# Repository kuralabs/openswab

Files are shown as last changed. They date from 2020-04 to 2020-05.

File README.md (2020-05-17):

# OpenSwab - Hisopo Nasofaringeal (NP) para COVID-19

[][cc-by-sa]

[English Version](README.en.md)

[Versión en PDF](doc/OpenSwab-Rev-4-KuraLabs.pdf)

## Descargo de responsabilidad

OpenSwab fue construido, diseñado y puesto a disposición en el contexto de una
escasez global de suministros y equipos para combatir la crisis de salud
pública causada por la enfermedad por Coronavirus (COVID-19). Este diseño,
junto con muchos otros, está siendo revisado actualmente por las autoridades
sanitarias y está siendo sometido a ensayos clínicos.

**SIN EMBARGO, NO HA SIDO PROBADO, VALIDADO O APROBADO TOTALMENTE POR NINGUNA
ORGANIZACIÓN. POR LO TANTO, DEBE SER CONSIDERADO UN PROTOTIPO.**

KuraLabs S.R.L comparte estos diseños en buena voluntad con la comunidad global
en un momento de crisis con el fin de enfrentar las brechas en la respuesta
regional y ofrecer un método alternativo para producir hisopos de prueba
necesarios utilizados para probar casos sospechosos de COVID-19 que están
siendo requeridos con urgencia. En consecuencia, KuraLabs S.R.L no asume
**NINGUNA RESPONSABILIDAD** por las lesiones o daños directos, indirectos o
incidentales sufridos como resultado del uso, mal uso o dependencia de estos
hisopos de prueba y/o de la información y el contenido de este sitio web.

La principal prioridad para KuraLabs S.R.L es el bienestar de los pacientes. En
consecuencia, es responsabilidad de quien quiera utilizar OpenSwab de enviarlo
para su aprobación, revisión y ensayos clínicos respectivos con el fin de
obtener una licencia, autorización o aprobación por parte de su autoridad
reguladora local antes de usar estos hisopos en el contexto médico. Al decidir
voluntariamente usar y/o producir los diseños de OpenSwab, usted asume el
riesgo de cualquier lesión resultante. **ÚSELO BAJO SU PROPIO RIESGO**.

## Descripción

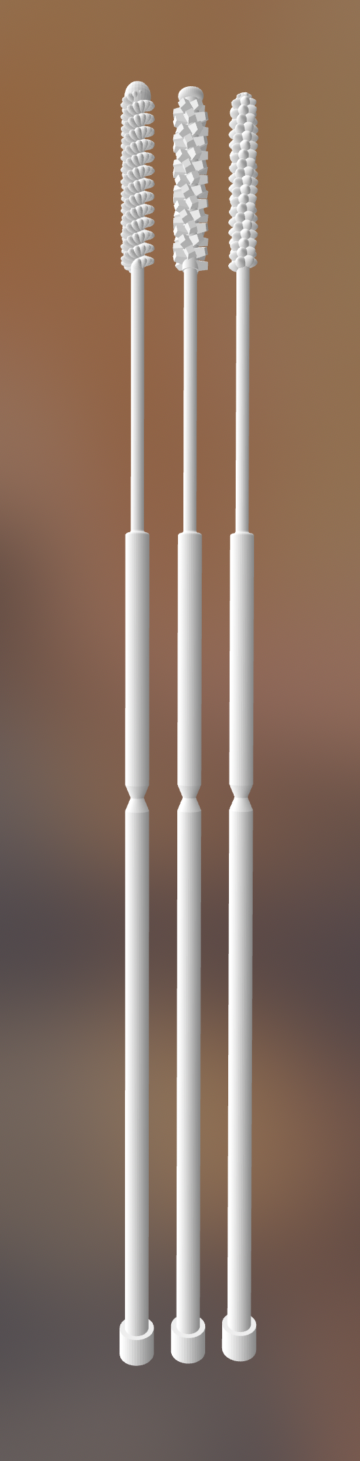
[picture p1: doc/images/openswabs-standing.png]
OpenSwab Render


OpenSwab es un prototipo de hisopo nasofaringeal (NP) diseñado para recolectar
muestras y realizar pruebas de COVID-19.

Es un hisopo fino y flexible, el cual es insertado en la cavidad nasal de forma
paralela a la parte inferior de la fosa nasal hasta que la cabeza del hisopo
toque la pared de la nasofaringe. Al llegar a la pared, se procede a realizar
pequeñas rotaciones de forma que la cabeza del hisopo recolecte el material
biológico requerido para proceder a realizar la prueba COVID-19.

Los hisopos utilizados para pruebas COVID-19 no pueden estar hechos de
materiales como algodón o madera, ya que los mismos afectan el ARN de la
muestra tomada.

Debido a la precisión y exactitud requerida, este hisopo fue diseñado para ser
impreso por una impresora 3D de tecnología SLA (Estereolitografía) utilizando
resina de curado ultravioleta (UV) biocompatible de Clase I (uso de corto plazo)
resistente al calor para su posterior esterilización en un autoclave.

Al momento de escribir este artículo, existe una escasez global de equipo de
protección personal y otros suministros médicos, incluidos los hisopos de
prueba. Estos hisopos fueron diseñados y creados en un esfuerzo por
proporcionar una posible solución alternativa a este problema.

La propiedad intelectual de este diseño se encuentra bajo una licencia
[CC BY-SA 4.0][cc-by-sa] por lo que puede ser utilizado, producido, modificado
y comercializado libremente. Puede referirse a la sección de licencia o
contactar al equipo de OpenSwab para más información.

<br clear="right"/>

## Fotos

<p align="center">
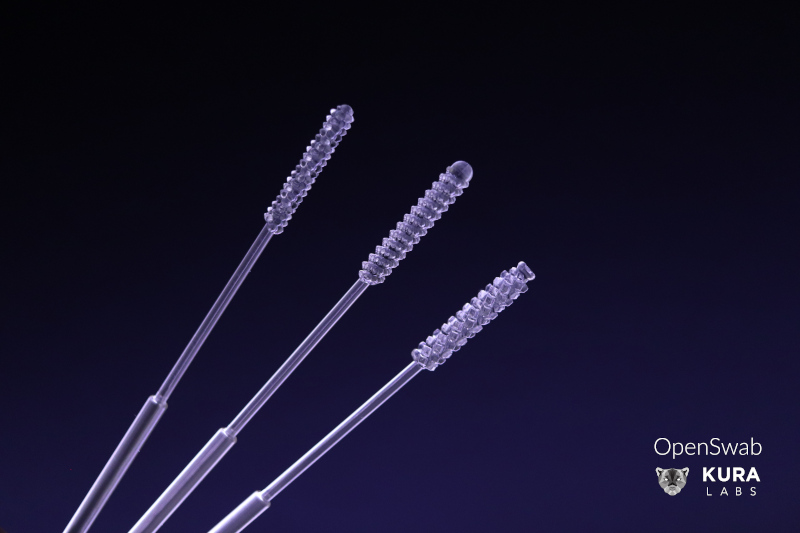
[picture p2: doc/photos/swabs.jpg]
OpenSwab swabs
  
</p>

<br clear="right"/>

<p align="center">
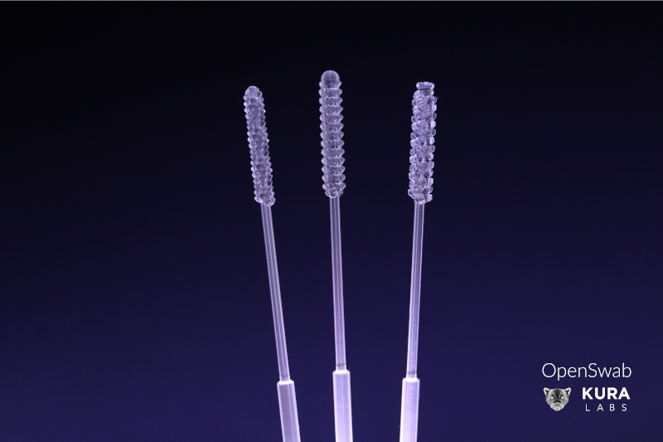
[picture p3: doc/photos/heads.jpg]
OpenSwab heads
  
</p>

<br clear="right"/>

<p align="center">
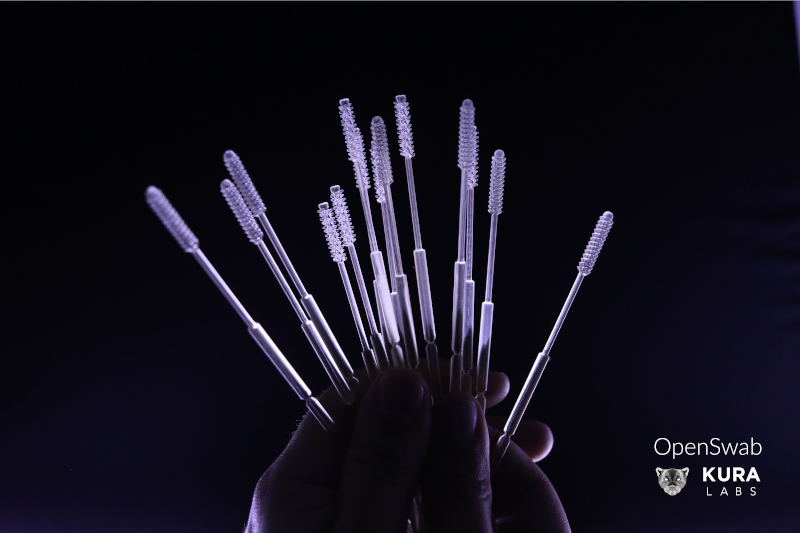
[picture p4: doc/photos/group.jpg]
OpenSwab group
  
</p>

<br clear="right"/>

## Especificaciones Técnicas

OpenSwab ofrece cuatro modelos con diferentes versiones de cabeza para la
recolección de muestras, denominadas "Bristle", "Pyramid", "Vitellus".

<p align="center">
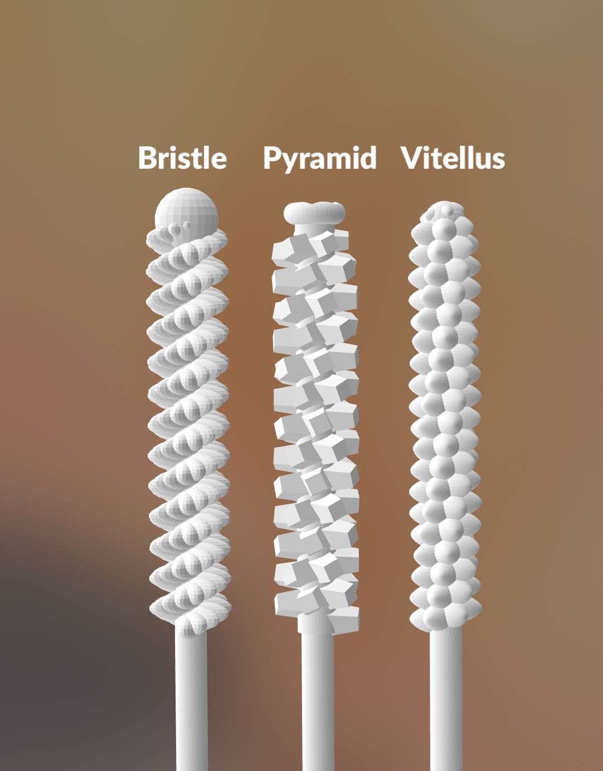
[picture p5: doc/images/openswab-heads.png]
OpenSwab Heads
    
</p>

| Modelo             | Bristle         | Pyramid                      | Vitellus        |
| ------------------ | --------------- | -----------------------------| ----------------|
| *Público meta*     | Adulto          | Adulto                       | Adulto          |
| *Uso*              | Nasofaringeal   | Nasofaringeal                | Nasofaringeal   |
| *Altura total*     |         145.0mm |                      145.0mm |         145.0mm |
| *Material*         | Resina UV 405nm | Resina UV 405nm              | Resina UV 405nm |
| *Esterilización*   | Autoclave       | Autoclave                    | Autoclave       |
|                                               **Cabeza**                              |
| *Textura*          | Hojuela         | Pirámide truncada            | Elipsoide       |
| *Patrón*           | Helicoidal      | Helicoidal                   | Helicoidal      |
| *Terminación*      | Esférica        | Toroide con estrella convexa | Esférica        |
| *Diámetro interno* |           1.5mm |                       1.85mm |           1.5mm |
| *Diámetro externo* |           3.9mm |                        3.9mm |           3.9mm |
| *Largo*            |          20.0mm |                       20.0mm |          20.0mm |
|                                            **Cuello flexible**                        |
| *Diámetro*         |           1.5mm |                        1.5mm |           1.5mm |
| *Largo*            |          30.0mm |                       30.0mm |          30.0mm |
|                                               **Cuerpo**                              |
| *Diámetro*         |          2.75mm |                       2.75mm |          2.75mm |
| *Largo*            |          95.0mm |                       95.0mm |          95.0mm |
| *Punto de quiebre* |          95.0mm |                       95.0mm |          95.0mm |

Todas estas dimensiones son fácilmente configurables.
Ver sección de [Configuración del Producto](#configuracion-del-producto).

## Características del Producto

- Punto de Quiebre: Al finalizar la toma de la muestra, el punto de quiebre
  permite separar la parte del hisopo que se encarga de la recolección del
  material biológico para así almacenarla en el tubo de muestra.

  El punto de quiebre también funciona como guía visual para indicarle al
  personal médico que debe evitar manipular el hisopo pasando el mismo, tanto
  para evitar la contaminación de la muestra como para prevenir cualquier tipo
  de exposición.

- Material de Construcción: Los hisopos utilizados para pruebas COVID-19 no
  pueden estar hechos de materiales como algodón o madera, ya que los mismos
  afectan el ARN (Ácido Ribonucléico) de la muestra tomada.

  Es por eso que OpenSwab está diseñado para ser impreso en una impresora 3D de
  tecnología SLA (Estereolitografía) utilizando resina de curado ultravioleta
  (UV) biocompatible de Clase I (uso de corto plazo) resistente al calor para
  su posterior esterilización en un autoclave.

- Diseño anatómico: Hisopo diseñado con un cuello delgado y flexible que se
  adapta a las fosas nasales del paciente por lo que se reduce el malestar y
  facilita el posicionamiento de la cabeza en el lugar adecuado por parte del
  personal médico. La cabeza cuenta además con un patrón helicoidal que
  facilita la introducción, el retiro y la acción giratoria propia del frotis.

- Diseño ergonómico: Pensado en un diámetro y largo adecuado para su
  manipulación por parte del personal encargado de la prueba.

- Fácil configuración de dimensiones: OpenSwab está diseñado de forma que los
  parámetros de las dimensiones del hisopo sean fácilmente configurables según
  sea necesario, lo que permitirá en el futuro crear una versión especial para
  niños y niñas.

- Facilidad de producción: OpenSwab puede fabricarse con impresoras 3D de
  tecnología SLA comerciales accesibles como la Anycubic Photon o la Creality
  LD-002R. El largo del hisopo es compatible con la gran mayoría del área de
  impresión de éstas impresoras, que normalmente soportan un máximo de 150mm de
  altura.

## Fabricación

Los archivos `exports/openswab-*.stl` contienen las versiones exportadas de los
modelos 3D en formato STL listos para ser impresos. El archivo
[`exports/openswab-printable.stl`](exports/openswab-printable.stl) contiene
un arreglo con las 4 versiones de OpenSwab en caso de ser requerido.

Las *estimaciones* de fabricación de un lote de OpenSwabs en diferentes
impresoras 3D se listan a continuación:

### Creality LD-002R

- **Tamaño de cama de impresión:** *120 x 68 x 160mm*.
- **Tamaño del lote:** *12x16*.
- **Cantidad de hisopos producidos:** *72*.
- **Recina requerida:** *80.2ml*.
- **Tiempo de impresión:** *10h38m11s*.

### Anycubic Photon

- **Tamaño de cama de impresión:** *120 × 68 × 150mm*.
- **Tamaño del lote:** *12x16*.
- **Cantidad de hisopos producidos:** *72*.
- **Recina requerida:** *80.2ml*.
- **Tiempo de impresión:** *10h38m11s*.

<p align="center">
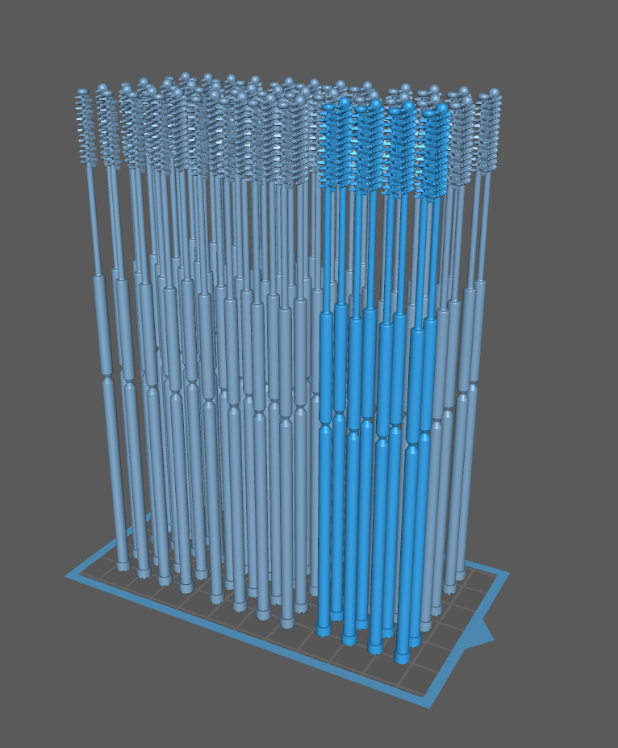
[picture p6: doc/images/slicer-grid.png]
Batch of OpenSwabs
    
</p>

## Configuración del Producto

OpenSwab fue diseñado en su totalidad utilizando el Software Libre
[OpenSCAD](https://www.openscad.org/), por lo que para su modificación o
reproducción no se requiere de la adquisición de licencias de Software de pago.

El archivos fuente de los diseños se encuentra en este repositorio con una
extensión `.scad`. El archivo principal es [`custom.scad`](custom.scad) y al
abrirlo se pueden modificar todos los parámetros del mismo fácilmente desde la
ventana del customizador.

<p align="center">
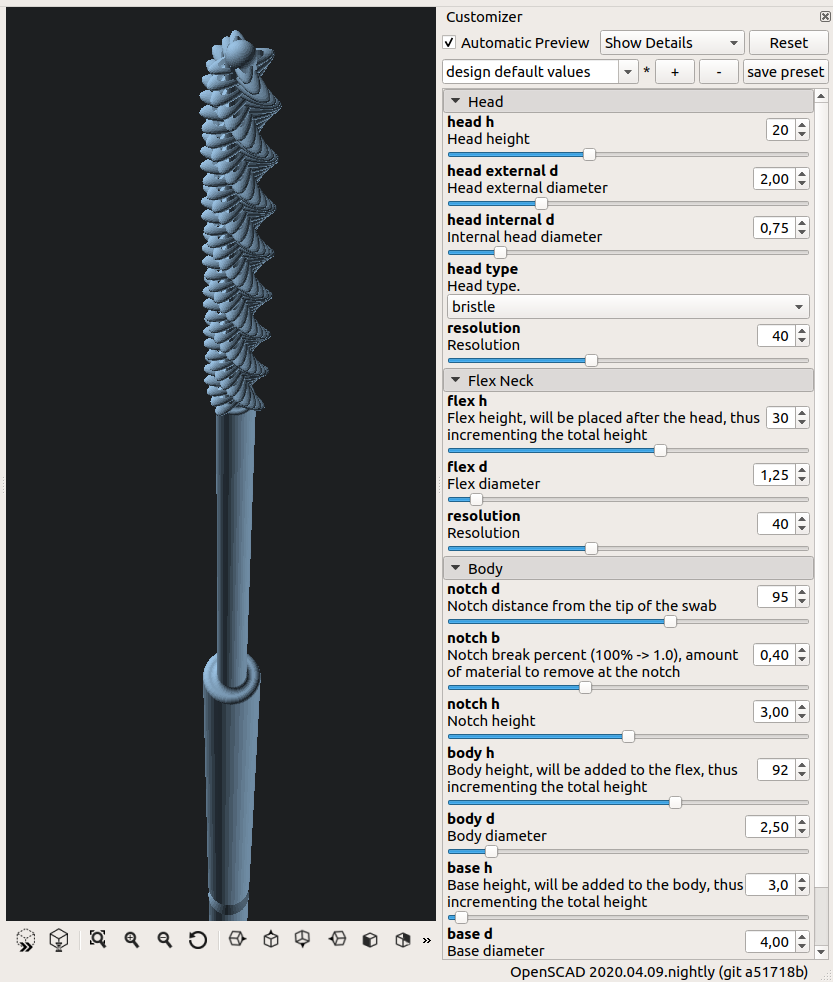
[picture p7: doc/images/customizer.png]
OpenSwab in OpenSCAD Customizer
    
</p>

## Referencias

- Interim Guidelines for Collecting, Handling, and Testing Clinical Specimens
  from Persons for Coronavirus Disease 2019 (COVID-19) (10 de abril de 2020).
  https://www.cdc.gov/coronavirus/2019-nCoV/lab/guidelines-clinical-specimens.html

- Centers for Disease Control and Prevention (CDC) Pertussis Testing Video:
  Collecting a Nasopharyngeal Swab Clinical Specimen (10 de abril de 2020).
  https://youtu.be/zqX56LGItgQ

- How to Collect Nasopharyngeal Samples for Flu Testing (Dr. Bonner Series)
  (10 de abril de 2020). https://youtu.be/v5A4H9q4JVA

- NETEC: COVID-19 Laboratory Specimen Collection: Nasopharyngeal Swab - Flyer
  and Validation Checklist (10 de abril de 2020).
  https://repository.netecweb.org/items/show/894

- NETEC: COVID-19 Laboratory Specimen Collection: Nasopharyngeal Swab
  (10 de abril de 2020). https://repository.netecweb.org/items/show/840

## Licencia

La propiedad intelectual de este diseño se encuentra bajo una licencia
internacional [CC BY-SA 4.0][cc-by-sa] por lo que puede ser utilizado,
fabricado, reproducido, modificado y comercializado libremente.

Todo trabajo derivado debe indicar "Basado en OpenSwab" y un link al sitio web
https://github.com/kuralabs/openswab, así como ser compartido bajo los mismos
términos de uso.

OpenSwab fue diseñado en su totalidad utilizando el Software Libre
[OpenSCAD](https://www.openscad.org/), por lo que para su impresión y
modificación no se requiere de la adquisición de licencias de Software de pago.

KuraLabs S.R.L se reserva el derecho de presentar y solicitar una patente para
cualquier diseño, algoritmo, forma o característica patentable que esté
presente o se derive de la Propiedad Intelectual (PI) presentada como parte de
OpenSwab. Si se concede, si corresponde, KuraLabs S.R.L garantiza que
**NO UTILIZARÁ** su derecho de hacer cumplir tales patentes o solicitar
licencias a cualquier persona o empresa que utilice cualquier PI de OpenSwab en
cualquier contexto, incluido el uso comercial. Además, KuraLabs S.R.L
presentaría dichas patentes a un repositorio de patentes defensivas con el
objetivo final de mejorar el acceso a la PI médica en los países en desarrollo
y ayudar a construir una robusta colección de arte previo para proteger el uso
de estos dispositivos.

En este contexto, KuraLabs SRL se une a la iniciativa propuesta por el
Presidente de Costa Rica, el Presidente Carlos Alvarado, y el Ministro de
Salud, Daniel Salas, plasmada en una carta enviada el 23 de marzo de
2020[[1]][presidencia-cr] a la Organización Mundial de la Salud (OMS) para
crear un repositorio de propiedad intelectual de tecnologías para la detección,
prevención, control y tratamiento de la pandemia del COVID-19 con el fin de
proporcionar acceso gratuito o licencias en términos razonables y accesibles
para todos los países. Dicha propuesta fue apoyada posteriormente por la OMS,
como lo declaró su Director General Tedros Adhanom Ghebreyesus en la
conferencia de prensa del 6 de abril de 2020 "Muchas gracias, señor Presidente.
Apoyo esta propuesta, y estamos trabajando con Costa Rica para finalizar los
detalles. [...] Pido a todos los países, empresas e instituciones de
investigación que apoyen los datos abiertos, la ciencia abierta y la
colaboración abierta para que todas las personas puedan disfrutar de los
beneficios de la ciencia y la investigación".[[2]][who-briefing]

OpenSwab fue diseñado desde cero en Costa Rica.

```
Copyright (C) 2020 KuraLabs S.R.L

Usted acepta y acuerda estar obligado por los términos y condiciones de esta
Licencia Internacional Pública de Atribución/Reconocimiento-CompartirIgual 4.0
de Creative Commons ("Licencia Pública"). En la medida en que esta Licencia
Pública pueda ser interpretada como un contrato, a Usted se le otorgan los
Derechos Licenciados en consideración a su aceptación de estos términos y
condiciones, y el Licenciante le concede a Usted tales derechos en consideración
a los beneficios que el Licenciante recibe por poner a disposición el Material
Licenciado bajo estos términos y condiciones.

    https://creativecommons.org/licenses/by-sa/4.0/

```

[][cc-by-sa]

[cc-by-sa]: http://creativecommons.org/licenses/by-sa/4.0/
[cc-by-sa-image]: https://licensebuttons.net/l/by-sa/4.0/88x31.png
[cc-by-sa-shield]: https://img.shields.io/badge/License-CC%20BY--SA%204.0-lightgrey.svg
[presidencia-cr]: https://www.presidencia.go.cr/comunicados/2020/03/costa-rica-submits-proposal-for-who-to-facilitate-access-to-technologies-to-combat-covid-19/
[who-briefing]: https://www.who.int/dg/speeches/detail/who-director-general-s-opening-remarks-at-the-media-briefing-on-covid-19---6-april-2020

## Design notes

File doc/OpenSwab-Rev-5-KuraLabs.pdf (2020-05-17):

## OpenSwab Rev 5

16 de Mayo del 2020

## _____________________________________________________

## Descargo de Responsabilidad

OpenSwab fue construido, diseñado y puesto a disposición en el contexto de una escasez global de suministros y equipos para combatir la crisis de salud pública causada por la enfermedad por Coronavirus (COVID-19). Este diseño, junto con muchos otros, está siendo revisado actualmente por las autoridades sanitarias y está siendo sometido a ensayos clínicos.

SIN EMBARGO, NO HA SIDO PROBADO, VALIDADO O APROBADO TOTALMENTE POR NINGUNA ORGANIZACIÓN. POR LO TANTO, DEBE SER CONSIDERADO UN PROTOTIPO.

KuraLabs S.R.L comparte estos diseños en buena voluntad con la comunidad global en un momento de crisis con el fin de enfrentar las brechas en la respuesta regional y ofrecer un método alternativo para producir hisopos de prueba necesarios utilizados para probar casos sospechosos de COVID-19 que están siendo requeridos con urgencia. En consecuencia, KuraLabs S.R.L no asume NINGUNA RESPONSABILIDAD por las lesiones o daños directos, indirectos o incidentales sufridos como resultado del uso, mal uso o dependencia de estos hisopos de prueba y/o de la información y el contenido de este sitio web.

La principal prioridad para KuraLabs S.R.L es el bienestar de los pacientes. En consecuencia, es responsabilidad de quien quiera utilizar OpenSwab de enviarlo para su aprobación, revisión y ensayos clínicos respectivos con el fin de obtener una licencia, autorización o aprobación por parte de su autoridad reguladora local antes de usar estos hisopos en el contexto médico. Al decidir voluntariamente usar y/o producir los diseños de OpenSwab, usted asume elriesgo de cualquierlesión resultante. ÚSELO BAJO SU PROPIO RIESGO.

KuraLabs S.R.L
info@kuralabs.io

## _____________________________________________________

## Descripción

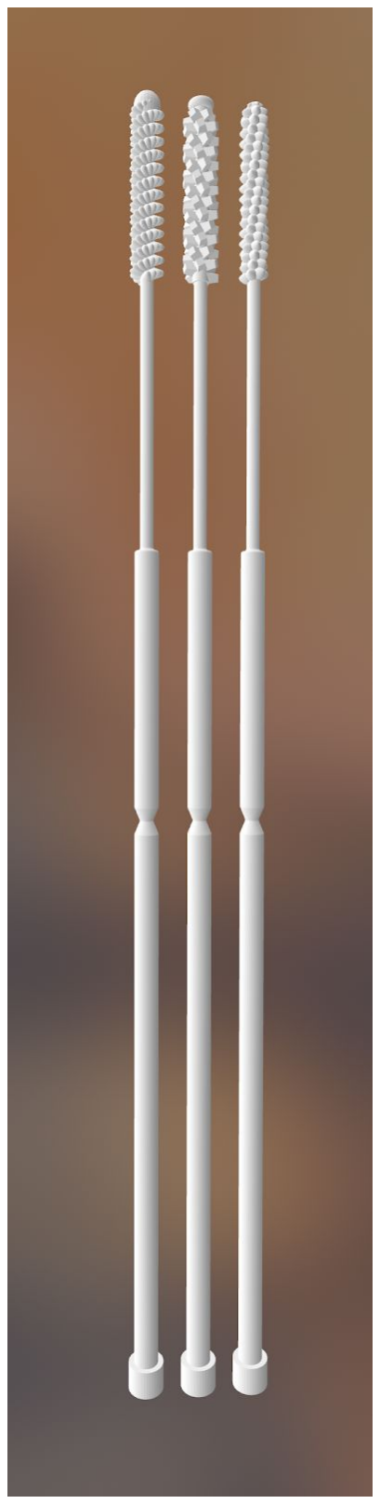
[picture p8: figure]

OpenSwab es un prototipo de hisopo nasofaringeal (NP) diseñado para recolectar muestras y realizar pruebas de COVID-19.

Es un hisopo fino y flexible, el cual es insertado en la cavidad nasal de forma paralela a la parte inferior de la fosa nasal hasta que la cabeza del hisopo toque la pared de la nasofaringe. Al llegar a la pared, se procede a realizar pequeñas rotaciones de forma que la cabeza del hisopo recolecte el material biológico requerido para proceder a realizarla prueba COVID-19.

Los hisopos utilizados para pruebas COVID-19 no pueden estar hechos de materiales como algodón o madera, ya que los mismos afectan el ARN de la muestra tomada.

Debido a la precisión y exactitud requerida, este hisopo fue diseñado para ser impreso por una impresora 3D de tecnología SLA (Estereolitografía) utilizando resina de curado ultravioleta (UV) biocompatible de Clase I (uso de corto plazo) resistente al calor para su posterior esterilización en un autoclave.

Al momento de escribir este artículo, existe una escasez global de equipo de protección personal y otros suministros médicos, incluidos los hisopos de prueba. Estos hisopos fueron diseñados y creados en un esfuerzo por proporcionar una posible solución alternativa a este problema.

La propiedad intelectual de este diseño se encuentra bajo una licencia CC BY-SA por lo que puede ser utilizado, producido, modificado y comercializado libremente. Puede referirse a la sección de licencia o contactar al equipo de OpenSwab para más información.

## _____________________________________________________

## Fotos

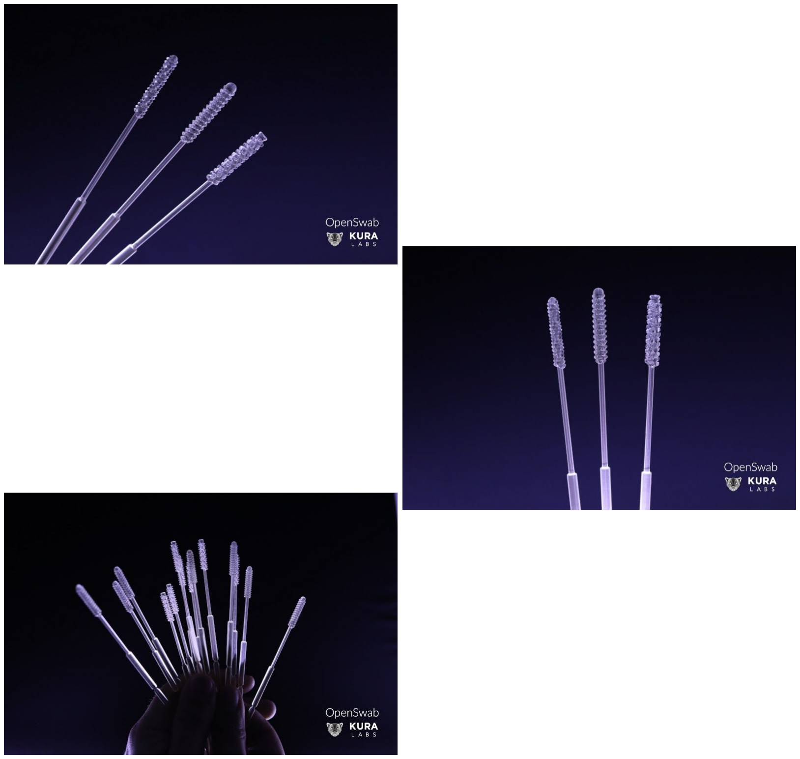
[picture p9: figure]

## _____________________________________________________

## Especificaciones Técnicas

OpenSwab ofrece cuatro modelos con diferentes versiones de cabeza para la recolección de muestras, denominadas "Bristle", "Pyramid" y "Vitellus"

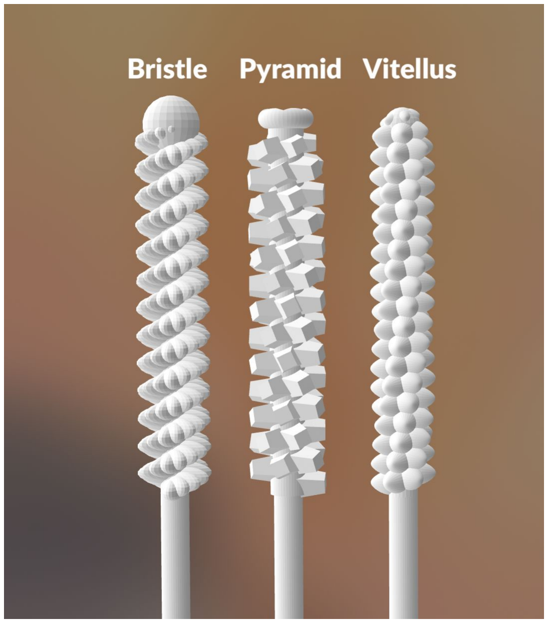
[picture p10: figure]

Modelo | Bristle | Pyramid | Vitellus
Público Meta | Adulto | Adulto | Adulto
Uso | Nasofaringeal | Nasofaringeal | Nasofaringeal
Altura total | 145.0mm | 145.0mm | 145.0mm
Material | Resina UV 405nm | Resina UV 405nm | Resina UV 405nm
Esterilización | Autoclave | Autoclave | Autoclave

## _____________________________________________________

Modelo | Bristle | Pyramid | Vitellus

Cabeza

Textura | Hojuela | Pirámide truncada | Elipsoide
Patrón | Helicoidal | Helicoidal | Helicoidal
Terminación | Esférica | Toroide con estrella convexa | Esférica
Diámetro interno | 1.5mm | 1.85mm | 1.5mm
Diámetro externo | 3.9mm | 3.9mm | 3.9mm
Largo | 20.0mm | 20.0mm | 20.0mm

Cuello flexible

Diámetro | 1.5mm | 1.5mm | 1.5mm
Largo | 30.0mm | 30.0mm | 30.0mm

Cuerpo

Diámetro | 2.75mm | 2.75mm | 2.75mm
Largo | 95.0mm | 95.0mm | 95.0mm
Punto de quiebre | 95.0mm | 95.0mm | 95.0mm

## _____________________________________________________

## Características del Producto

- Punto de Quiebre: Al finalizar la toma de la muestra, el punto de quiebre permite separar la parte del hisopo que se encarga de la recolección del material biológico para así almacenarla en el tubo de muestra.

El punto de quiebre también funciona como guía visual para indicarle al personal médico que debe evitar manipular el hisopo pasando el mismo, tanto para evitarla contaminación de la muestra como para prevenir cualquiertipo de exposición.

- Material de Construcción: Los hisopos utilizados para pruebas COVID-19 no pueden estar hechos de materiales como algodón o madera, ya que los mismos afectan el ARN (Ácido Ribonucléico) de la muestra tomada.

Es por eso que OpenSwab está diseñado para ser impreso en una impresora 3D de tecnología SLA (Estereolitografía) utilizando resina de curado ultravioleta (UV) biocompatible de Clase I (uso de corto plazo)resistente al calor para su posterior esterilización en un autoclave.

- Diseño anatómico: Hisopo diseñado con un cuello delgado y flexible que se adapta a las fosas nasales del paciente por lo que se reduce el malestar y facilita el posicionamiento de la cabeza en el lugar adecuado por parte del personal médico. La cabeza cuenta además con un patrón helicoidal que facilita la introducción, elretiro y la acción giratoria propia del frotis.
- Diseño ergonómico: Pensado en un diámetro y largo adecuado para su manipulación por parte del personal encargado de la prueba.
- Fácil configuración de dimensiones: OpenSwab está diseñado de forma que los parámetros de las dimensiones del hisopo sean fácilmente configurables según sea necesario, lo que permitirá en el futuro crear una versión especial para niños y niñas.
- Facilidad de producción: OpenSwab puede fabricarse con impresoras 3D de tecnología SLA comerciales accesibles como la Anycubic Photon o la Creality LD-002R. El largo del hisopo es compatible con la gran mayoría del área de impresión de éstas impresoras, que normalmente soportan un máximo de 150mm de altura.

## _____________________________________________________

## Fabricación

Los archivos | exports/openswab-*.stl | contienen las versiones exportadas de los modelos 3D en formato
STL listos para ser impresos. El archivo | exports/openswab-printable.stl | contiene un arreglo con las 4
versiones de OpenSwab en caso de serrequerido.

Las estimaciones de fabricación de un lote de OpenSwabs en diferentes impresoras 3D se listan a continuación:

### Creality LD-002R

- Tamaño de cama de impresión: 120 × 68 × 160mm.
- Tamaño del lote: 12x16.
- Cantidad de hisopos producidos: 72.
- Recina requerida: 80.2ml.
- Tiempo de impresión: 10h38m11s.

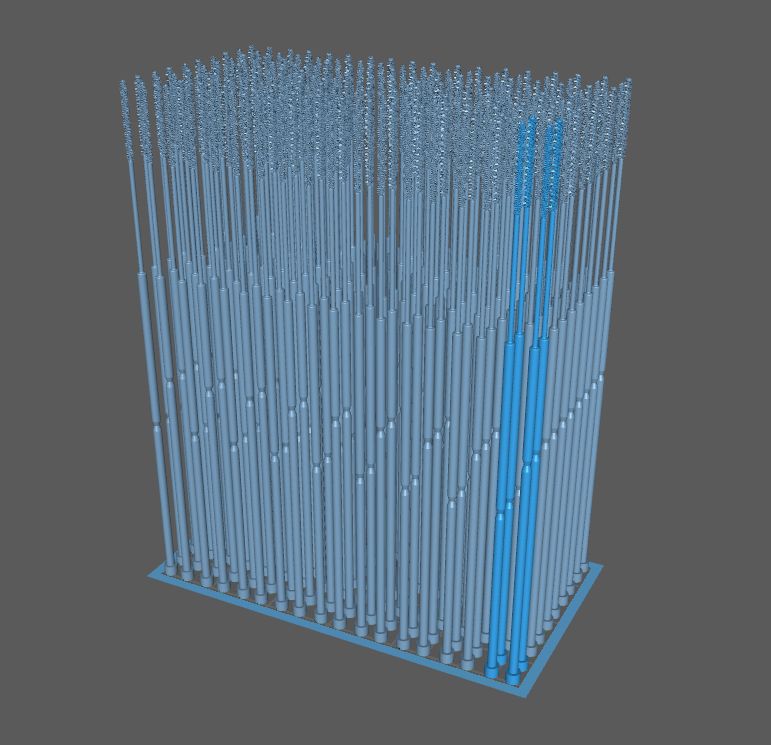
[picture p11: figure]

### Anycubic Photon

- Tamaño de cama de impresión: 120 × 68 × 150mm.
- Tamaño del lote: 12x16.
- Cantidad de hisopos producidos: 72.
- Recina requerida: 80.2ml.
- Tiempo de impresión: 10h38m11s.

## _____________________________________________________

## Configuración del Producto

OpenSwab fue diseñado en su totalidad utilizando el Software Libre OpenSCAD, (https://www.openscad.org/) por lo que para su modificación o reproducción no se requiere de la adquisición de licencias de Software de pago.

El archivos fuente de los diseños se encuentra en este repositorio con una extensión .scad. El archivo principal es custom.scad (https://github.com/kuralabs/openswab/blob/master/custom.scad) y al abrirlo se pueden modificartodos los parámetros del mismo fácilmente desde la ventana del customizador.

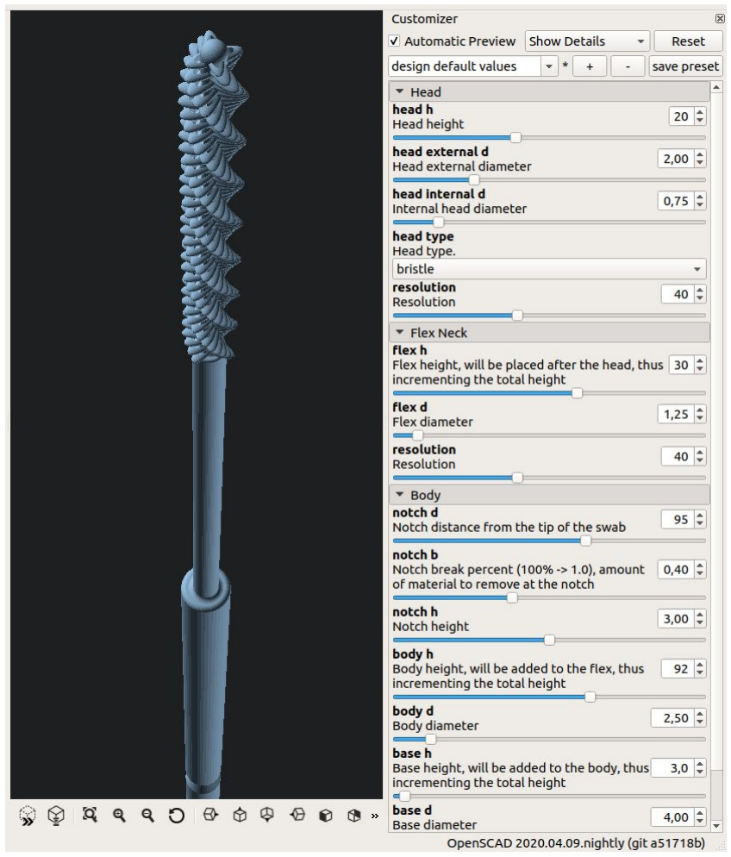
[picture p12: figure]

## _____________________________________________________

## Referencias

- Interim Guidelines for Collecting, Handling, and Testing Clinical Specimens from Persons for Coronavirus Disease 2019 (COVID-19) (10 de abril de 2020). https://www.cdc.gov/coronavirus/2019-nCoV/lab/guidelines-clinical-specimens.html
- Centers for Disease Control and Prevention (CDC) Pertussis Testing Video: Collecting a Nasopharyngeal Swab Clinical Specimen (10 de abril de 2020). https://youtu.be/zqX56LGItgQ
- How to Collect Nasopharyngeal Samples for Flu Testing (Dr. Bonner Series) (10 de abril de 2020). https://youtu.be/v5A4H9q4JVA
- NETEC: COVID-19 Laboratory Specimen Collection: Nasopharyngeal Swab - Flyer and Validation Checklist (10 de abril de 2020). https://repository.netecweb.org/items/show/894
- NETEC: COVID-19 Laboratory Specimen Collection: Nasopharyngeal Swab (10 de abril de 2020). https://repository.netecweb.org/items/show/840

## _____________________________________________________

## Licencia

La propiedad intelectual de este diseño se encuentra bajo una licencia internacional CC BY-SA 4.0 (http://creativecommons.org/licenses/by-sa/4.0/) por lo que puede ser utilizado, fabricado,reproducido, modificado y comercializado libremente.

Todo trabajo derivado debe indicar "Basado en OpenSwab" y un link al sitio web https://github.com/kuralabs/openswab, así como ser compartido bajo los mismos términos de uso.

OpenSwab fue diseñado en su totalidad utilizando el Software Libre OpenSCAD, (https://www.openscad.org/) por lo que para su impresión y modificación no se requiere de la adquisición de licencias de Software de pago.

KuraLabs S.R.L se reserva el derecho de presentar y solicitar una patente para cualquier diseño, algoritmo, forma o característica patentable que esté presente o se derive de la Propiedad Intelectual (PI) presentada como parte de OpenSwab. Si se concede, si corresponde, KuraLabs S.R.L garantiza que NO UTILIZARÁ su derecho de hacer cumplir tales patentes o solicitar licencias a cualquier persona o empresa que utilice cualquier PI de OpenSwab en cualquier contexto, incluido el uso comercial. Además, KuraLabs S.R.L presentaría dichas patentes a un repositorio de patentes defensivas con el objetivo final de mejorar el acceso a la PI médica en los países en desarrollo y ayudar a construir una robusta colección de arte previo para proteger el uso de estos dispositivos.

En este contexto, KuraLabs SRL se une a la iniciativa propuesta por el Presidente de Costa Rica, el Presidente Carlos Alvarado, y el Ministro de Salud, Daniel Salas, plasmada en una carta enviada el 23 de marzo de 2020[1] a la Organización Mundial de la Salud (OMS) para crear un repositorio de propiedad intelectual de tecnologías para la detección, prevención, control y tratamiento de la pandemia del COVID-19 con el fin de proporcionar acceso gratuito o licencias en términos razonables y accesibles para todos los países. Dicha propuesta fue apoyada posteriormente por la OMS, como lo declaró su Director General Tedros Adhanom Ghebreyesus en la conferencia de prensa del 6 de abril de 2020 "Muchas gracias, señor Presidente. Apoyo esta propuesta, y estamos trabajando con Costa Rica para finalizar los detalles. [...] Pido a todos los países, empresas e instituciones de investigación que apoyen los datos abiertos, la ciencia abierta y la colaboración abierta para que todas las personas puedan disfrutar de los beneficios de la ciencia y la investigación".[2]

OpenSwab fue diseñado desde cero en Costa Rica.

[1] - COSTA RICA SUBMITS PROPOSAL FOR WHO TO FACILITATE ACCESS TO TECHNOLOGIES TO COMBAT COVID-19 https://www.presidencia.go.cr/comunicados/2020/03/costa-rica-submits-proposal-for-who-to-facilitate-access-to-technologies-to-combat-covid-19/
[2] -WHO DIRECTOR-GENERAL'S OPENING REMARKS AT THE MEDIA BRIEFING ON COVID-19 - 6 APRIL 2020 https://www.who.int/dg/speeches/detail/who-director-general-s-opening-remarks-at-the-media-briefing-on-covid-19---6-april-2020

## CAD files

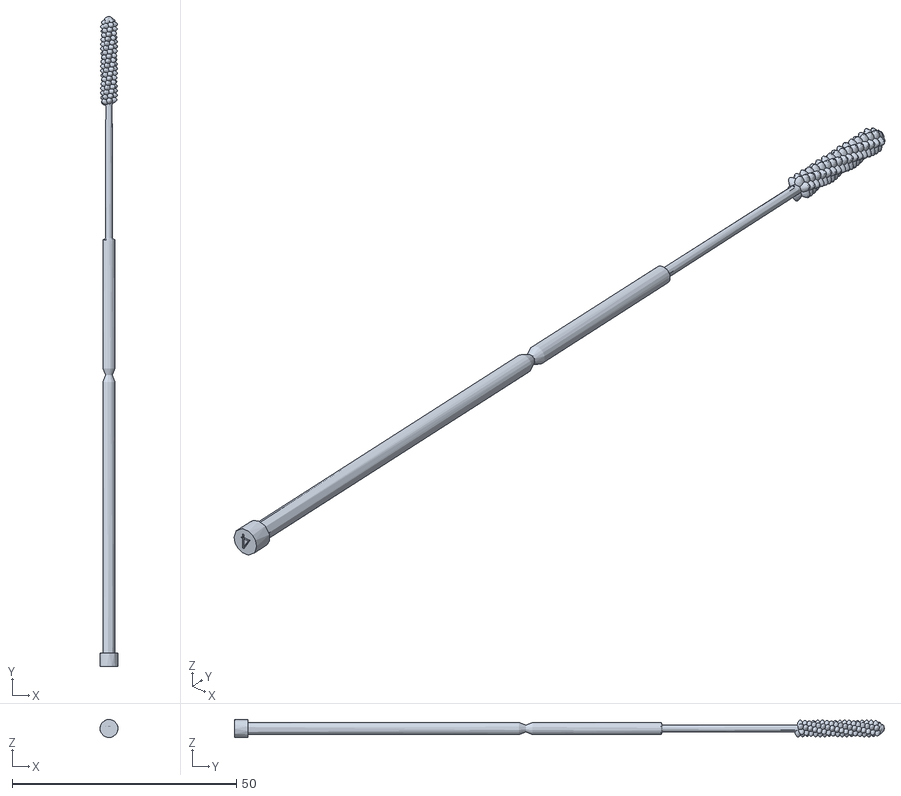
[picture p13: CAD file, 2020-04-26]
exports/objs/openswab-vitellus.obj
4.03 x 145.0 x 4.03

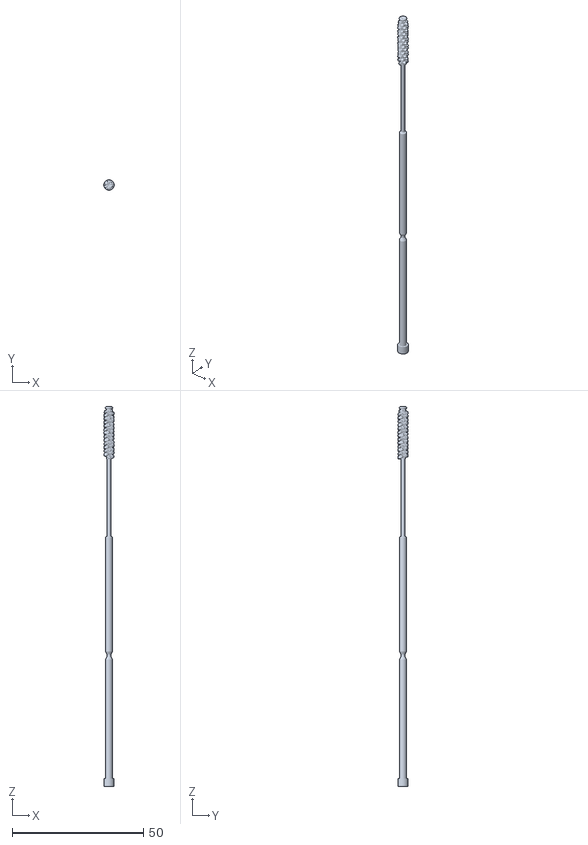
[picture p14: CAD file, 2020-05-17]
exports/openswab-pyramid.stl
4.03 x 4.03 x 145.0

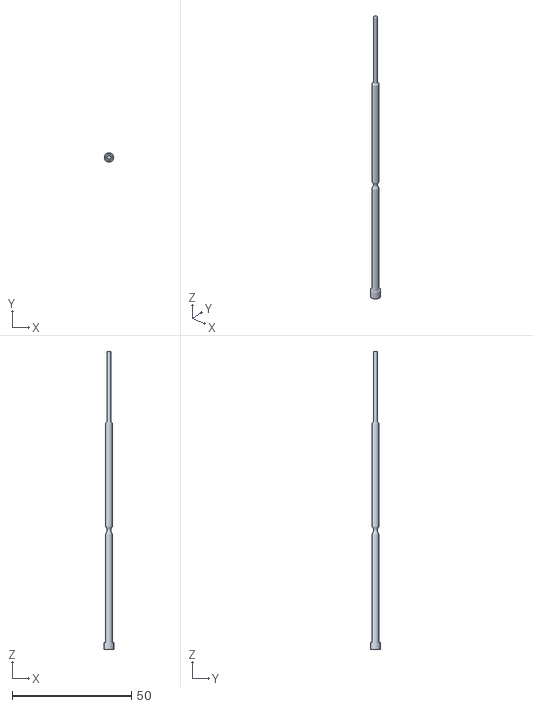
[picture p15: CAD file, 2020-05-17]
exports/body.stl
4.00 x 4.00 x 125.0

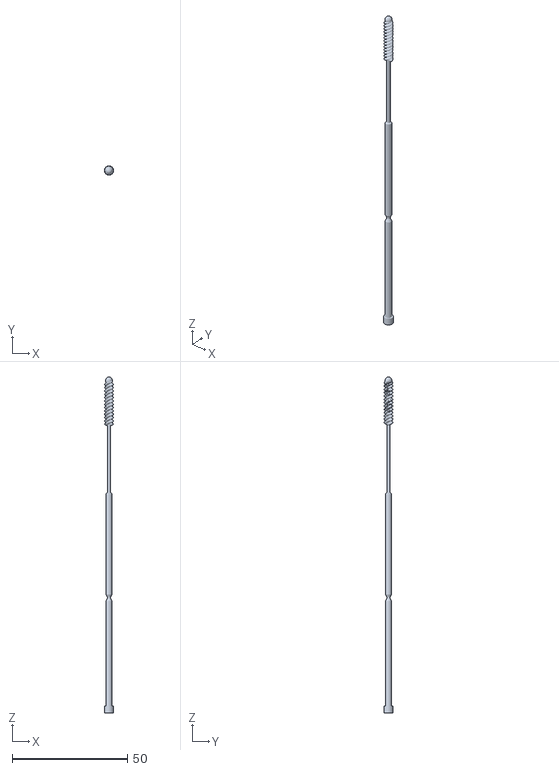
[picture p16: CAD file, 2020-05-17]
exports/openswab-bristle.stl
4.00 x 4.00 x 145.7

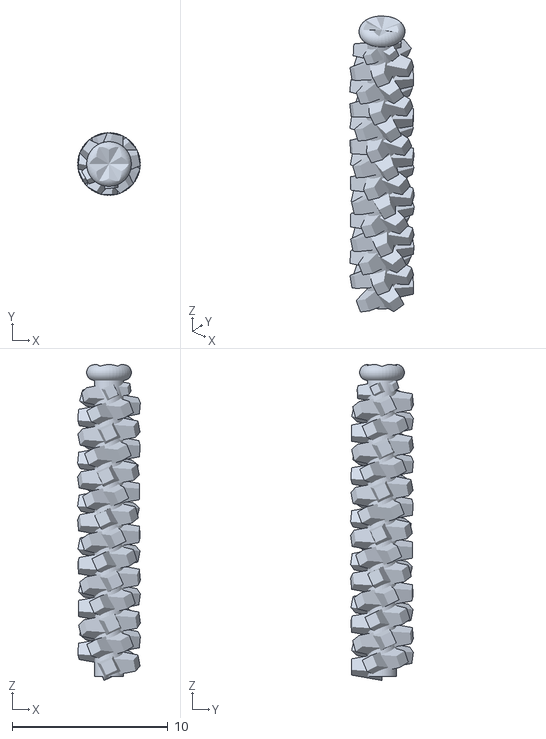
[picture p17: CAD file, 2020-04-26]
exports/head-pyramid.stl
4.03 x 4.03 x 20.3

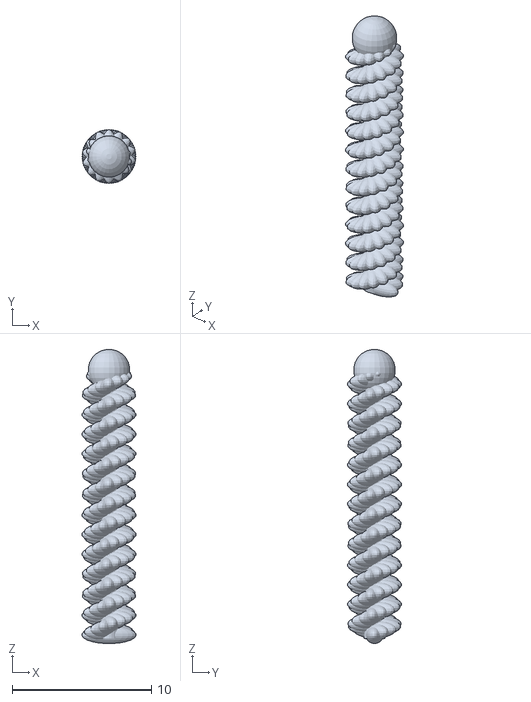
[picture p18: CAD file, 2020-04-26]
exports/head-bristle.stl
3.87 x 3.87 x 21.1

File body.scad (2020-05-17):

use <library.scad>;


module body(
    // Head height
    head_h=20.0,
    // Head diameter
    head_d=1.5,

    // Flex height, will be placed after the head, thus incrementing the total height
    flex_h=30.0,
    // Flex diameter
    flex_d=1.5,

    // Notch distance from the tip of the swab
    notch_d=95.0,
    // Notch break percent (100% -> 1.0), amount of material to remove at the notch
    notch_b=0.455,
    // Notch height
    notch_h=3.0,
    // Notch extension
    notch_e=0.75,

    // Body height, will be added to the flex, thus incrementing the total height
    body_h=92.0,
    // Body diameter
    body_d=2.75,

    // Base height, will be added to the body, thus incrementing the total height
    base_h=3.0,
    // Base diameter
    base_d=4.0,
) {
    total_height = head_h + flex_h + body_h + base_h;

    // Transition smoother
    translate([0, 0, base_h + body_h + flex_h])
        smoother(flex_d, head_d);

    // Flex
    translate([0, 0, base_h + body_h])
        cylinder(h=flex_h, d=flex_d);
    translate([0, 0, base_h + body_h])
        smoother(external_d=body_d, internal_d=flex_d);

    // Body
    difference() {
        translate([0, 0, base_h])
            cylinder(h=body_h, d=body_d);
                // The notch
        translate([0, 0, total_height - notch_d])
            notch(
                external_d=body_d,
                internal_d=body_d - body_d * notch_b,
                height=notch_h,
                extension=notch_e
            );
    }

    // Base
    difference() {
        cylinder(h=base_h, d=base_d);

        // Revision number
        revision = 4;

        rotate([0, 180, 0]) color("red")
            linear_extrude(height=1, center=true)
                text(
                    str(revision),
                    size=base_d * 0.6,
                    halign="center",
                    valign="center"
                );
    }
}


body($fn=40);

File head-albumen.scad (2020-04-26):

use <library.scad>;


module helicoid(
    radius=8,
    thickness=1.25,
    height=50,
    twists=2
) {
    for (clockwise = [true, false])
        for (angle = [0, 90, 180, 270])
            rotate([0, 0, angle]) coil(
                 r1=radius - (thickness / 2),
                 r2=thickness / 2,
                 h=height,
                 clockwise=clockwise,
                 twists=twists
            );
}



module albumen_head(
    // Head height
    head_h=20.0,
    // Head external diameter
    head_external_d=3.9,
    // Internal head diameter
    head_internal_d=1.5,

    // Albumen configuration
    albumen_head_fn=13,
    albumen_twists=1.249,
) {
    half_tip = head_external_d / 2;
    tip_start = head_h - half_tip;

    cylinder(h=tip_start, d=head_internal_d);
    translate([0, 0, tip_start])
        sphere(d=head_external_d, $fn=albumen_head_fn);

    translate([0, 0, half_tip])
        sphere(d=head_external_d, $fn=albumen_head_fn);

    translate([0, 0, half_tip])
    helicoid(
        radius=half_tip,
        thickness=head_external_d - head_internal_d,
        height=tip_start - half_tip,
        twists=albumen_twists
    );
}


albumen_head($fn=40);

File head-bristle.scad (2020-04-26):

use <library.scad>;


/**
 * Generate a hollow oval shape.
 */
module oval_hollow_bristle(extension=2.0, thickness=0.5, width=1, ratio=0.8) {
    render() {
        difference() {
            scale([extension, width, thickness])
                sphere(d=1);
            scale([extension * ratio, width * ratio, thickness])
                cylinder(h=1, d=1, center=true);
        }
    }
}

/**
 * Generate a oval shape.
 */
module oval_bristle(extension=2.0, thickness=0.5, width=1) {
    render() {
        scale([extension, width, thickness])
            sphere(d=1);
    }
}


module bristle_head(
    // Head height
    head_h=20.0,
    // Head external diameter
    head_external_d=3.9,
    // Internal head diameter
    head_internal_d=1.5,

    // Spiral configuration
    z_step=0.20,
    angle_step=25,
    scale_step=-0.065,
    step_correction=-1,
    scale_correction=-5,

    // Bristle configuration
    bristle_t=1.25,
    bristle_w=1.25,
) {
    tip_start = head_h - head_internal_d / 2;

    cylinder(h=tip_start, d=head_internal_d);
    translate([0, 0, tip_start])
        sphere(head_internal_d);

    spiral(
        step_max=head_h / z_step + step_correction,
        z_step=z_step,
        angle_step=angle_step,
        scale_step=scale_step,
        scale_start=tip_start / z_step + scale_correction
    ) {
        translate([0, 0, 0.25])
            oval_bristle(
                extension=head_external_d,
                thickness=bristle_t,
                width=bristle_w
            );
    };
}


bristle_head($fn=24);

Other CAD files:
exports/openswab-albumen.stl
head-pyramid.scad
exports/objs/openswab-bristle.obj
exports/objs/openswab-pyramid.obj
head-vitellus.scad
library.scad
shapes.scad
swab.scad

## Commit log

2020-04-07 Initial prototype.
    [swab.scad]
2020-04-11 Improves body with notch, flexible shaft and modular heads.
    [head.scad, shapes.scad, swab.scad]
2020-04-11 Adds head and spiral module for head pattern generation.
    [head.scad, shapes.scad, swab.scad]
2020-04-11 Adds Bristle head.
    [head.scad, shapes.scad]
2020-04-11 Adds final rendering of the swabs using both Pyramid and Bristle swab heads.
    [head.scad, shapes.scad, swab.scad]
2020-04-11 Updates prototype documentation.
2020-04-11 Adds prototype documentation in Spanish
2020-04-11 Modularizes heads and body.
    [body.scad, head-bristle.scad, head-pyramid.scad, head.scad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]
2020-04-12 Exports Head Pyramid.
    [head-pyramid.3mf, head-pyramid.stl]
2020-04-12 Exports Body.
    [body-80.stl, body-95.3mf, body-95.stl]
2020-04-12 Adds exports for OpenSwab with Pyramid head @ 95mm.
2020-04-12 Reduces the detail of the models to improve rendering.
    [body.scad, head-bristle.scad, head-pyramid.scad, swab.scad]
2020-04-12 Adds support for the OpenSCAD Customizer.
    [custom.scad]
2020-04-12 Removes 3MF exports as OpenSCAD fails to generate them, import the STLs instead.
    [body-95.3mf, head-bristle.scad, head-pyramid.3mf]
2020-04-12 Add STL files for all 4 swab models.
    [openswab-pyramid-80.stl]
2020-04-12 Shortening the OpenSwab default height to 145mm for safer printing.
    Many SLA printers like the Anycubic Photon have a 150mm height printing area.
    [body-80.stl, body-95.stl, body.scad, custom.scad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]
2020-04-12 Updates STL files to match new dimensions for safer printing.
    [openswab-pyramid-80.stl, openswab-pyramid-95.stl]
2020-04-13 Updates body and flex diameter to make it thinner.
    [body.scad]
2020-04-13 Smooth flex to head transition.
    [body.scad]
2020-04-13 Modify bristle head to match new diameters.
    [head-bristle.scad, library.scad]
2020-04-13 Modify pyramid head to match new diameters.
    [head-pyramid.scad]
2020-04-13 Update swab default values to match new diameter.
    [custom.scad, swab.scad]
2020-04-13 Generate STL files with new thinner diameter.
    [body-80.stl, body-95.stl]
2020-04-13 Generates updated full swab STLs.
    [openswab-pyramid-80.stl, openswab-pyramid-95.stl]
2020-04-13 Fix bad default values for the heads.
    [custom.scad, swab.scad]
2020-04-15 Modifies diameters in head, flex, body and base after first printing try"
    [body-80.stl, body-95.stl, body.scad, body.stl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]
2020-04-15 Adds updated STL printable version.
2020-04-24 Moves specific modules to their main file and updates default head_external_d to 4.0.
    [custom.scad, head-bristle.scad, head-pyramid.scad, library.scad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]
2020-04-24 New head "Vitellus" added.
    [custom.scad, head-vitellus.scad, swab.scad]
2020-04-24 Removes custom.scad and centralizes all customization in swab.scad.
    [custom.scad, swab.scad]
2020-04-26 Adds Bristle head with new 4mm diameter
2020-04-26 Back to basics: return of the initial head, new codename "Albumen".
    [head-albumen.scad, library.scad]
2020-04-26 Fixes wrong final height in vitellus.
    [head-vitellus.scad]
2020-04-26 Add optimized STL heads.
    [head-pyramid.stl]
2020-04-26 New diameters in the body shape to make it a little bit more flexible.
    [body.scad, body.stl, swab.scad]
2020-04-26 Fixes albumen height issues.
    [head-albumen.scad]
2020-04-26 Adds support to the new albumen head to the options in the swab.
    [swab.scad]
2020-04-26 Adds revision number to the bottom of the body.
    [body.scad, body.stl]
2020-04-26 Updates Vitellus head render to latest version.
    [head-vitellus.scad]
2020-04-26 Fixes Vitellus head to have 3.9 diameter.
    [head-vitellus.scad]
2020-04-26 Adds new Swabs STL for all models
    [openswab-albumen.stl, openswab-bristle.stl, openswab-pyramid.stl]
2020-04-26 Adjusts Body 2.75mm diameter
    [body.scad, body.stl, swab.scad]
2020-04-26 Adjusts Pyramid head 3.9mm diameter
    [head-pyramid.scad, head-pyramid.stl, openswab-pyramid.stl]
2020-04-26 Adjusts Albumen head 3.9mm diameter
    [head-albumen.scad, openswab-albumen.stl]
2020-04-26 Adjusts Bristle head 3.9mm diameter
    [head-bristle.scad, head-bristle.stl, openswab-bristle.stl]
2020-04-26 Updates the printable STL to include all latest version of all heads.
2020-04-26 Added swabs obj files.
    [openswab-bristle.obj, openswab-pyramid.obj, openswab-vitellus.obj]
2020-04-26 Updates printable version to include latest Vitellus.
2020-05-17 Changes breakpoint to 95mm and with a 0.75mm extension.
    [body.scad, body.stl, library.scad, openswab-albumen.stl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]
